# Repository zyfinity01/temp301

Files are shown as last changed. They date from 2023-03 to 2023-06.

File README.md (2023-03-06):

# Open Data Recorder for Environmental Monitoring

An open source and open hardware IoT-connected SDI-12-enabled remote data recorder capable of deployment for environmental monitoring by New Zealand Regional Councils.

## Quick Links

- [Project Charter](docs/charter.md)
- [Meetings](https://gitlab.ecs.vuw.ac.nz/engr489-environment-monitoring/engr489-project/issues?scope=all&utf8=%E2%9C%93&state=all&label_name%5B%5D=Meeting)
- [Development Guide](docs/technical/README.md)

## Project Description

Regional Councils maintain large environmental monitoring networks with real-time data recorded by data recorders being reported via telemetry to virtual servers at a data centre.

This project arose from the desire of the Hydrology Team at Greater Wellington Council to explore the benefits that IoT technologies could offer &mdash; low-cost hardware, low power consumption, future-proof communication technologies and the ability of Council staff to extend the capabilities of the data recorder &mdash; whilst maintaining the sensor accuracy required for scientific studies and regulatory functions. In collaboration with staff and students at the School of Engineering and Computer Science at Victoria University of Wellington, a prototype data recorder has been developed to meet the environmental monitoring requirements of they Hydrology Team.

## Project Requirements

Overarching project requirements are listed in [docs/requirements/requirements.md](docs/requirements/requirements.md).

- Revision 3 requirements are listed in [docs/requirements/requirements_for_Rev 3.0](docs/requirements/requirements_for_Rev 3.0).
- Revision 4 requirements are the same as Revision 3.

## Overall Objectives

- Develop a system to enable more cost effective collection of data to serve the Region's environmental data needs.
- Deliver an 'Open-Source' system that is fully documented which will allow GWRC staff to up-skill and understand IoT concepts and provide GWRC IT department the ability to support the server and data transfer components in the future. Hardware construction would need to be well documented to allow future production of devices post-project.
- Enable future development of the system in collaboration with VUW.
- Develop a system that could be offered to other Regional Councils around New Zealand if successful.

The project can be as big or as small as the project team decides. The main thing is to ensure we end up with a robust, accurate system that can be evaluated against our current systems. GWRC will be able to provide test sites locations and VUW project team will be able exposed to the work the council undertakes - Field trip(s)?

GWRC doesn't have any set funding for the project and monetary contributions can be discussed if the project is of interest to VUW. I should imagine GWRC would be able to pay for the virtual server chargers, software licences and hardware but that is to be confirmed with management.

## Repository Directory Structure

### High level overview

```text
Environmental-Monitoring-2020/engr489-project/
├── docs
├── software
    ├── device
        ├── embedded
        └── webapp
    ├── server
    └── simulator
├── hardware
├── util
└── venv
```

### `software`: Embedded Software and Device Simulators

#### `device`: Embedded Software, Web-App Code

```text
device
├── build
├── embedded
└── webapp
```

- `build`: automatically created by the software build script, `build.sh`.
- `embedded`: Micropython device code &mdash; development takes place here.
- `webapp`: preact web app code &mdash; development takes place here.

#### `server`: scripts for communication with remote servers

```text
server/
[no subdirectories]
```

Python scripts for publishing to an MQTT broker and subscribing to topics. Also contains a Python script for publishing to Microsoft Power BI <https://powerbi.microsoft.com/>. Used during exploration of different protocols for transmitting data from the data recorder.

#### `simulator`: Simulation Scripts

```text
simulator/
[no subdirectories]
```

Various scripts for simulating different parts of the project.

### `docs`: Documents and Documentation

```text
docs
├── bom
├── datasheets
├── development
├── literature
├── meetings
├── presentations
├── reports
├── requirements
├── research
└── technical
```

- `bom`: Bill of Materials (BoM) documents sent for PCB manufacture.
- `technical`: technical documentation, including documentation of the tinyweb server implementation which runs on the ESP32 to provide a web interface to the data recorder.
- `literature`: A flat folder containing PDF copies of anything that will or could be cited in the reports: journal articles, tech notes, etc.  There should be a BibTeX .bib bibliography file at the same level as the PDF files, for use with the JabRef open source bibliography and reference manager.
- `meetings`: saved emails from the 2021 Honours project.
- `presentations`: The files used in any presentations, including the ENGR 489 course final presentation.
- `reports`: Contains the ENGR 489 course reports. There are two reports required this year, a Preliminary Report and a Final Report. LaTeX source files. R, Matlab, etc. files, containing only the figures used in the report at this level. One sub-folder "Figures" to keep figures organised.
- `requirements`: documentation provided by the clients for project requirements.
- `research`: Embedded software, Web App, Hardware Design and PCB development notes.

### `hardware`: Data Recorder Hardware

```text
hardware/
├── reviews
└── schematics
```

- `reviews`: documentation of schematics and PCB reviews.
- `schematics`: electronic schematics and PCB designs of the current revision.

### `util`: utility scripts

```text
util/
├── Docker
├── ansible
├── micropython-hitl
├── micropython-software
├── scripts
└── vagrant
```

Build and test scripts, including development and test environment provisioning and configuration scripts, for performing utility functions separate from the software running on the data recorder.

- `Docker`: Dockerfiles to create images used in jobs in the GitLab CI pipeline.
- `ansible`: Ansible playbooks for provisioning development, build and test environments.
- `micropython-hitl`: hardware-in-the-loop (HTL) testing scripts.
- `micropython-software`: Dockerfile for running MicroPython in a Docker container for development and test purposes.
- `scripts`: build and test scripts mostly intended to be run in the CI pipeline.
- `vagrant`: Vagrantfile for testing of provisioning and configuration of HTL build and test servers in a VirtualBox VM.

### `venv`: Python Virtual Environment

Python virtual environment created when the instructions in the _Development Environment_ section of the [Technical Documentation](docs/technical/README.md) are followed.

---

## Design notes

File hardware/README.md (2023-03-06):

# Hardware

Information about the design of the hardware and evaluation can be found in this repository.

We are using KiCad 6.0. For migrate Altium project to KiCad. KiCad 6.0 is not backward-compatible, please update you KiCad to 6.0 to view the schematics and PCB layout.

- [Schematics](schematics/)
- [Reviews](reviews/)
- [Evaluation](power_consumption_Rev3)

---

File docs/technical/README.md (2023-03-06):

# Technical documentation

This directory stores the technical documentation for the project.

Subdirectories and pages:

- **architecture** - Architectural Documents.
  - **configuration** - device software configuration outline
  - **embedded_sw_architecture_** - outline of the embedded device software architecture
  - **webapp_architecture** - outline of the webapp architecture (frontend)
  - **webserver** - REST API reference for the on-device web-server
- **dev_environment_setup** - instructions for getting started with this repository
- **hardware_setup** - instructions for setting up the device hardware
- **micropython_build** - instructions for building micropython from source and uploading custom firmware to the device

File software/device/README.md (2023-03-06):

# Device Software

This directory holds the following subdirectories and files:

```text
device
├── build/
├── embedded/
├── webapp/
└── build.sh
```

- `build`: automatically created by the software build script, `build.sh` (see below).
- `embedded`: Micropython device code &mdash; development takes place here.
- `webapp`: preact web app code &mdash; development takes place here.
- `build.sh`: a build script that combines the output of the build scripts in the subdirectories, `build-webapp.sh` and `build-device.sh`, into a ready-to-upload `build/` directory with compiled micropython and preact code.

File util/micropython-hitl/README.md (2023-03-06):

# HITL Testing

## Resources

- [good introduction to using rshell](https://blog.miguelgrinberg.com/post/micropython-and-the-internet-of-things-part-iii-building-a-micropython-application)

## Process

HITL (Hardware in the loop testing) is a method of testing that integrates real hardware in the test process.
The `hitl-tests.sh` script first uploads the latest code to the device using `rshell`, then uses `pyboard.py` to copy the device test suite into ram and then run it.
The script greps the test output for "FAIL" and returns an error code if failures were found.

## Runner Setup

The HITL runner is currently on a raspbery pi model 3 B+ with a fresh install of Rasbian Buster.

Setup instructions:

Connect the HITL device via USB. Install apt package `picocom` and test serial communication works with `pycocom /dev/ttyUSB0`

Install gitlab-runner

```shell
curl -L https://packages.gitlab.com/install/repositories/runner/gitlab-runner/script.deb.sh | sudo bash
sudo apt-get install -y gitlab-runner
```

Register the runner

```shell
sudo gitlab-runner register
```

Add gitlab-runner user to dialout and tty groups

```shell
sudo usermod -aG dialout gitlab-runner
sudo usermod -aG tty gitlab-runner
```

Manually install packages onto the runner

```shell
sudo pip3 install pyboard rshell
```

---

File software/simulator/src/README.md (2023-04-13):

# Simulators

This directory contains two scripts:

- `device.py` - A device simulator, used for generating random data for testing the cloud components of this project
- `webserver.py` - A [flask](https://flask.palletsprojects.com/en/2.1.x/)-based script intended to be an API-compatible simulator for the device web-backend. It's used to test the web-app frontend.

Note: Ensure you have your virtual environment initialised and dependendencies from the top-level `requirements.txt` installed.

## Device Simulator

<!-- Refer to #548 -->

### Device Simulator Setup and Execution

1. Copy `device.example.conf` to `device.conf` and edit the defaults (if required)
1. run `python simulator.py [--help]`

### Configuration

| config option | default | description                                                                          |
|---------------|---------|--------------------------------------------------------------------------------------|
| port          | 1883    | broker port                                                                          |
| wait-time     | 3       | number of seconds to wait between attempting to send each message                    |
| device-type   | sdi-12  | type of device (can either be `sdi-12` or `rainfall`                                 |
| verbose       | False   | verbose logging                                                                      |
| format        | json    | Message format (json or csv)                                                         |

## Webserver Simulator

No setup is required to run the `webserver.py` script. Note, however, that paths to the webapp and configuration files are hard-coded into the script.

The simulator can be run from the command line, while at the repository top-level, by executing the command `python software/simulator/src/webserver.py` which will produce the following output (example):

```shell
$ python software/simulator/src/webserver.py
 * Loading JSON from software/device/embedded/src/services/config.example.json
 * Loading JSON from software/device/embedded/src/services/data.example.json
 * Serving Flask app 'webserver' (lazy loading)
 * Environment: production
   WARNING: This is a development server. Do not use it in a production deployment.
   Use a production WSGI server instead.
 * Debug mode: on
 * Running on http://127.0.0.1:5000 (Press CTRL+C to quit)
 * Restarting with stat
 * Loading JSON from software/device/embedded/src/services/config.example.json
 * Loading JSON from software/device/embedded/src/services/data.example.json
 * Debugger is active!
 * Debugger PIN: xxx-yyy-zzz
```

As indicated in the Flask output, the webapp can be viewed by visiting <http://127.0.0.1:5000> in a web browser. Web server activity will be logged to the terminal (example):

```shell
127.0.0.1 - - [10/Oct/2022 15:07:14] "GET / HTTP/1.1" 200 -
127.0.0.1 - - [10/Oct/2022 15:07:15] "GET /bundle.b5e19.css HTTP/1.1" 200 -
127.0.0.1 - - [10/Oct/2022 15:07:15] "GET /bundle.2dea9.esm.js HTTP/1.1" 200 -
127.0.0.1 - - [10/Oct/2022 15:07:15] "GET /data HTTP/1.1" 200 -
127.0.0.1 - - [10/Oct/2022 15:07:15] "GET /config HTTP/1.1" 200 -
127.0.0.1 - - [10/Oct/2022 15:07:15] "GET /favicon.ico HTTP/1.1" 200 -
127.0.0.1 - - [10/Oct/2022 15:07:15] "GET /assets/icons/apple-touch-icon.png HTTP/1.1" 200 -
```

The `webserver.py` simulator may be exited by pressing `Ctrl-C`.

---

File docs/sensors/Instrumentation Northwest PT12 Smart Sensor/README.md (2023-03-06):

# Instrumentation Northwest

The Instrumentation Northwest Inc. sondes made available to us for development and evaluation are PT12 pressure and temperature Smart Sensors.

Instrumentation Northwest, Inc. <https://web.archive.org/web/20180330105810/http://inwusa.com/> became Seametrics <https://www.seametrics.com/> by 1 May 2018. Only a couple of PDFs are downloadable from the Internet Archive page for the PT12 sensor [2].

Seametrics' page has specifications and instructions for the latest version of the PT12 [3] which have been downloaded to this directory.

1. Products - Smart Sensors <https://web.archive.org/web/20160221212342/http://inwusa.com/products/smart-sensors/>
1. Smart Sensors - Pressure & Level - PT12 <https://web.archive.org/web/20160308074848/http://inwusa.com/products/smart-sensors/pressure-and-level/pt12/>
1. PT12 Pressure & Temperature with Modbus & SDI-12 Interface <https://www.seametrics.com/product/pt12/>

---

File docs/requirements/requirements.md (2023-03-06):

# Requirements

## Device Requirements

- Low powered
- Accurate timekeeping
  - Synced with time server
  - Timestamped to NZST (UTC+12)
  - Timestamp to nearest second
- Connected to 12V battery (lead acid, gel, AGM SLA)
  - Battery connected by screw/push terminal
  - Device should retain settings when powered down
  - Possibility of connecting solar panel or 12V AC adapter, so device should be capable of handling any voltage fluctuations
  - Overvoltage and reverse polarity protection
  - Lifetime of 3-6 months
- Wireless comms to mobile device for configuring
  - Bluetooth or WiFi
  - Activated by switch
- USB port for programming device (and maybe diagnostics)
- Wireless data transmission via Vodafone NB-IoT
  - Band 28
  - External antenna connection (SMA)
  - Data transfer protocol to ensure no data loss
- Appropriate size for fitting in raingauge or a galvanised pipe
- Consider ability to add Glyn pulse coherent radar
- Nice to have offline mode where device is out of range of NB-IoT
  - Removable modems to reduce cost of offline devices
  - Physical or in-app switch to toggle modem on/off.
  - Needs to have accurate timekeeping
- Data saved to device on SD card
  - Readings for each unique parameter will have an ID
  - Should contain ID, timestamp, reading
  - Needs accurate timekeeping
  - Need to be able to measure used/free space
- Cost between $200-$300 per device

### SDI-12

- Use SDI-12 communications protocol
- Relay to power up SDI-12 sensor
- User can schedule sensor readings manually
  - Device needs to automatically schedule readings to account for the time to start the sensor and take the reading

### Raingauge

- Ability to monitor 1 (preferably 2) inputs from reed switch triggering
  - With switch debounce
- Up to 1 reading per second
  - Timestamp to nearest second
- Send data every 5 minutes during rain, reduce to hourly (or 6-hourly) transmission when not raining

## Cloud Requirements

- Hosted on a virtual server
- Flexible data storage format to allow future integration with GWRC databases
- Explore possibility of enabling data transfer to FTP server using existing supplier's XML format
- View data in tabular and graph format
  - Identify missing data
  - Identify comms failure
- Send email/SMS for specific data
  - send for missing data, comms failure, system issues
- Daily transmission of SD card capacity

## App Requirements

### Configuration (App -> Device)

- Sensor Settings
  - Recording interval
  - Calibration multiplier (span)
  - Calibration offset (zero)
- Data transmission interval
- Physical location (use phone GPS) - optional
- Device ID and Name
- ability to put the device into "test mode" - temporarily disabling sending data to the cloud backend while calibrating the sensors
- send test message to cloud button
- Synchronise clock to cellphone clock. Useful for sites out of range of NB-IoT
- Set the SDI-12 sensor address on the app and specify ID of the variable being recorded - have a text name and the ability to specify units for measurement variables
- Some SDI-12 sensors take some time to boot up, so allow this time to be configured
- Assign units - mm/h for example

### Visualisation (Device -> App)

- No need to display graphs on the app, but do want live values
- Downloading device data from a specified interval
- number of sent/failed transmissions
- "Download all data" button
- most recent transmission
- most recent reading (for calibration)
- Device battery level
- Network reception level - Signal strength test (in -dBm) - only update this reading on request, no need to constantly poll
- Rainfall totals - because they visit every 2-3 months, they want to calibrate the total recorded rainfall against a level in a collection tank for QA purposes
- Used/free space on SD card

---

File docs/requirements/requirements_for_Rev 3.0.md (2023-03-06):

# Requirements

This document is about the requirements for the Rev 3.0 prototype.

- Improve power efficiency

  - All in one PCB (merge base board and extension board)
  - Use a different 12V to 5V regulator (TPS562201DDCR)
  - Upper limit of the current draw of the whole system is 8.2 mA

- Improve ease of use

  - Use fuel gauge IC to monitor battery state of charge (bq34z110)
  - Change though holes components (Inductors,RGB LEDs, hall effect sensors etc) to surface mount as well as ESP32 microcontroller
  - Use USB to UART interface for programming and debugging the ESP32

- Old problems to fix

  - Fix the reverse polarity protection (currently not working properly)
  - Fix the PCB layout of the power terminals (currently positive and negative labels are inverted)

- Environment Data

  - Water level, flow sensor
    - SDI-12 interface
    - Powered by 12V
  - Accurate timekeeping
    - Time from cellphone tower
    - Time from Real Time Clock (RTC)
  - Data saved to device on SD card
  - Rain gauge data
    - Record the pulse signal from rain gauge
    - Use external counter (flip-flops) circuit to store the data
    - Use a multiplexer to read the binary data when device wakeup
    - must be operating while microcontroller is in deep sleep

- Offline mode where device is out of range of any cellular network

  - Removable modems to reduce cost of offline devices
  - Physical or in-app switch to toggle modem on/off
  - Use onboard Real Time Clock (RTC) to have accurate timekeeping
  - Data storage on SD card

- Communication

  - Use u-box SARA-R4 NB-IoT modem
    - UART interface
    - Wireless data transmission via Vodafone NB-IoT
    - Wireless data transmission via Cat-M1 (Maybe)

- PCB Size

  - Appropriate size for fitting in rain gauge or a galvanised pipe
  - Approximately 13 cm x 17 cm

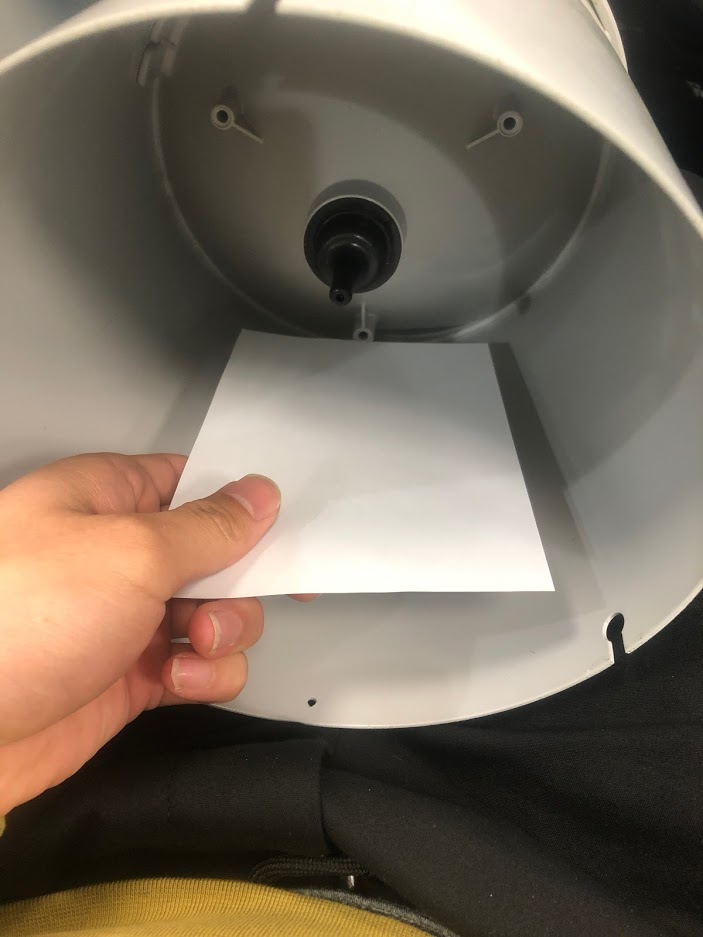
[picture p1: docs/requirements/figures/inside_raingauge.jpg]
Raingauge inside view


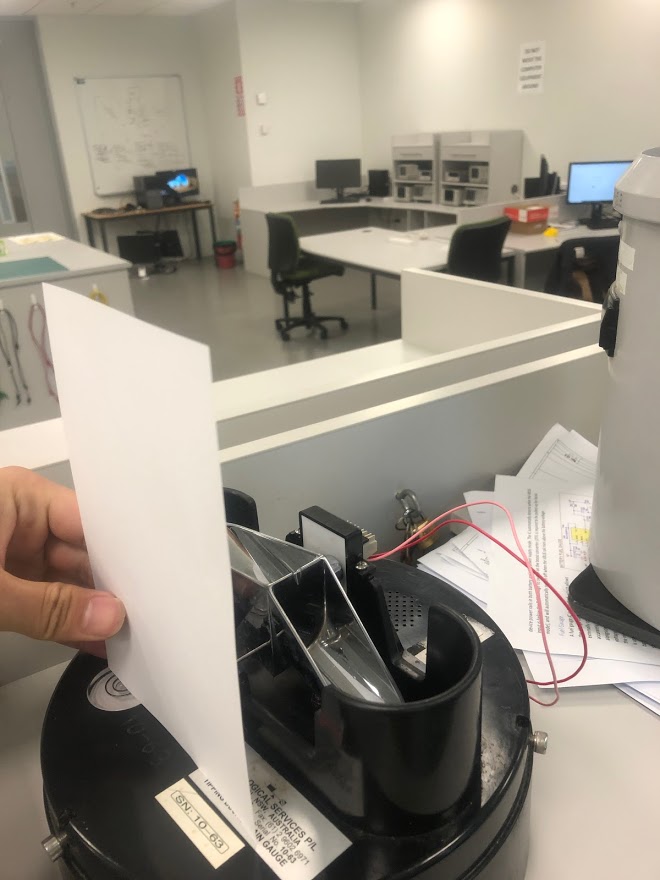
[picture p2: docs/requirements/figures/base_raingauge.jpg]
Raingauge base view


- Cost
  - Cost between $200-$300 per device

---

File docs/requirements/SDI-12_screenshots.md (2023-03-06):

# SDI-12 Configuration in HyQuest Data loggers

Screenshots to detail the process we would follow to achieve the outcomes we want with our current equipment.

We would power-up the SDI-12 sensor using the Digital Output (Relay supplying 12v) on a schedule. In the example below we’re assuming the sensor takes 20 secs to power up ready to take a measurement and we want the measurement taken on the prime 15 minute (0,15,30,45 mins).

HyQuest equipment only allow schedules to start and finish to a resolution of a minute so we would power up the sensor at 14 minutes ready for the 15 minute logged value.  We’d prefer to set schedules to the second resolution if possible?

The Sensor will be powered up for 120 secs and the process will be repeated every 15 minutes.



We set up the SDI-12 Device.

In this example it is a Shaft Encoder with address ‘zero’ and we’ve chosen to use the ‘M’ command for measurement.  Other options are ‘MC’ for measurement with checksum, ‘C’ for concurrent and ‘CC’ for concurrent with checksum (I think)

We’ve set the sensor up to send the measurement command to the SDI-12 device at 14mins 50 secs past the hour and then at an interval of 15 minutes onwards.  That gives the logger 10 secs to retrieve the measurement from the sensor before the data is ‘logged’ at the prime 15 minute interval.

There’s something going on behind-the-scenes at this point.  If we we’re sending the commands manually via a terminal program we’d have typed 0M!, to which the SDI-12 device will have replied with a string along the lines of 002.  The first zero is the SDI-12 device’s address followed by the number of seconds it will take the sensor to have a value ready for retrieval, in this case 2 seconds.

After waiting 2 seconds a zero would appear on the Terminal screen indicating the measurement has been taken. We’d then issue the ‘give me your data command’ 0D0! Would return the last reading from sensor address zero.  The device would then return the data string.

We don’t see any of that going on in the set-up page, so all that timing and back-and-forth must be programmed into the device.

**Note: The data strings retrieved from the device are saved to a temporary storage location in the logger.**



Next we set up the individual ‘sensors’ – basically the recorded variables / parameters from the different SDI-12 sensors attached to the device.

This example is Water level which is derived from SDI-12 sensor address ‘0’ which is aliased as ‘HS Shaft Encoder’ in the previous set-up screen. That isn’t really necessary for our device we could easily just use the address number.

Then we tell the device which variable we want to record from the returned data string from the sensor.  In this case water level is the first variable in the string.

We tell the logger that we want to apply a multiplier of 1000 (converting meters to millimetres) and an offset of zero to the returned value. **Note: Multiplier is always applied before offset in our calculations.**



Then we tell the logger how often we want the values to be recorded to the data logger’s permanent storage.  In this case every 15 minutes.

On the prime 15 minute mark, the data logger accesses the store string in the temporary storage location, extracts variable 1 applies the multiplier and offset calculations and stores the time-stamped value in it’s permanent memory.

**Note 1:** We **REALLY** like recording data on the prime minute (no seconds) with SDI-12 sensors. I guess it’s just ‘tidy’ so that values from different sensors / sites can be compared easily in data management suites, and for environmental monitoring a few seconds either way from the exact time isn’t all that important. It’s up to us to get the timing of sensor data retrieval as close to that prime point as possible.

That said if rounding to the minute is an issue on the device we could just accept that we’re having second values recorded and ‘knock’ them off in the data management on the server?

**Note 2:** We **REALLY** like recording rainfall data to the nearest second as the pulse is recorded on the device. This helps with sub-minute rainfall intensity analysis.



---

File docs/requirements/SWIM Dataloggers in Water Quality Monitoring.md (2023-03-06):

# Regional council use of continuous data loggers in water quality monitoring

The use of continuous loggers for water quality monitoring and investigations was discussed at the last SWIM meeting (3rd & 4th of May 2017). I also collated information of the LAWA website and contacted Environment Southland, the Otago Regional Council and the Greater Wellington Regional Council for information on their programmes.

In summary (Tables 1 and 2):

Many councils use sediment autosamplers, continuous DO sondes and turbidity loggers on a ‘roaming’ / investigation basis. Some councils (GW, ES, ORC, Horizons) started to use optical sensors for nitrate. ORC and ES reported good results for optical sensors, but not for ion selective electrodes (IS). Challenges are power supply and flow adjustment of continuous data. All lake buoys in shallow coastal lakes seem to include a phycocyanin (PC) sensor as proxy for cyanobacteria. Some trials are underway for continuous monitoring of E.coli (ColiMinder). Continuous monitoring has rarely been required as consent monitoring. A detailed list of equipment used by regional councils can be found in Table 3.

Additional notes from the SWIM meeting:

- NIWA is conducting a review of the ORC’s long term water quality monitoring.
- Dean Olson from the ORC pointed out issues comparing spot measurements vs. continuous data, as even the time of day the samples were collected can matter.
- Exo-NO3 was not recommended by GWRC, but others are happy with the YSI-Exo products in general.
- NIWA is trialling ColiMinder in Porirua for 3 years, Andrew Hughes and led by Megan Oliver at GWRC.
- NIWA is looking at relationship between turbidity and clarity in rivers to E. coli concentrations (Rob D-C).

**Table 1:** Regional Council use of continuous monitoring tools in lakes and coastal environments.

| Council | Lakes | Full WQ | Lake level | DO, temp | Turbidity | Comments |
| --- | --- | :---: | :---: | :---: | :---: | --- |
| **Northland** | Whangarei harbour, “buoys in estuaries” |  |  |  | &#x26AB; |  |  |
| **Auckland** | Pupuke (installed), Ototoa (scheduled) | &#x26AB; |  |  |  |  |  |
| **Waikato** | 4 lakes & 1 estuarine buoy | &#x26AB; |  |  |  |  |
| **Bay of Plenty 1** | Rerewhakaaitu, Okareka, Okataina, Rotoma, Rotomahana |  | &#x26AB; |  |  |  |
| **Bay of Plenty 1** | Okaro, Rerewhakaaitu, Rerewhakaaitu, Rotoiti, Rotorua, Tarawera | &#x26AB; |  |  |  | Operated by Waikato University or in partnership |
| **Hawkes Bay** | Lakes Waikaremoana, Tūtira |  |  | &#x26AB; |  | Also have coastal Exo sonde |
| **Horizons** | Horowhenua |  |  |  |  |  |
| **Wellington** | Wairapa (scheduled) | &#x26AB; |  |  |  | ColiMinder trial (NIWA) in Porirua harbour |
| **Tasman** | Maito Reservoir |  |  | &#x26AB; |  |  |
| **Environment Canterbury** | Ellesmere, Forsyth, Wainono | &#x26AB; |  |  |  |  |
| **Southland** | Manapouri (planned) shallow coastal lake (planned) | &#x26AB; |  |  |  |  |

**Note:** Water quality buoys (Full WQ) usually measure DO, temperature, chla, phycocyanin (PC) as proxy for cyanobacteria for coastal lakes, and can include lake level, conductivity, salinity and turbidity.

**Table 2:** Regional Council use of continuous monitoring tools in rivers – overview.

| Council | Flow | Temp | DO | Turbidity | Sediment | NO3 | EColi |
| --- | :---: | :---: | :---: | :---: | :---: | :---: | :---: |
| **Northland** |  |  |  | &#x26AB; | &#x26AB; |  |  |
| **Auckland** |  | &#x26AB; | &#x26AB; |  | &#x26AB; |  | <span style="border-radius:100%; background:orange;">&nbsp;&nbsp;&nbsp;&nbsp;</span> |
| **Waikato** | &#x26AB; | &#x26AB; | &#x26AB; | &#x26AB; | &#x26AB; |  |  |
| **Bay of Plenty**  | &#x26AB; | &#x26AB; | &#x26AB; | &#x26AB; | &#x26AB; | <span style="border-radius:100%; background:green;">&nbsp;&nbsp;&nbsp;&nbsp;</span> |  |
| **Hawkes Bay** | &#x26AB; |  | &#x26AB; |  | &#x26AB; |  |  |
| **Gisborne** | &#x26AB; |  |  |  |  |  |  |
| **Taranaki** |  | &#x26AB; | &#x26AB; | &#x26AB; |  |  |  |
| **Wellington** | &#x26AB; | &#x26AB; | &#x26AB; | &#x26AB; |  | <span style="border-radius:100%; background:orange;">&nbsp;&nbsp;&nbsp;&nbsp;</span> |  |
| **Horizons** | &#x26AB; |  | &#x26AB; |  |  | <span style="border-radius:100%; background:orange;">&nbsp;&nbsp;&nbsp;&nbsp;</span> | <span style="border-radius:100%; background:orange;">&nbsp;&nbsp;&nbsp;&nbsp;</span> |
| **Marlborough** |  | &#x26AB; | &#x26AB; | &#x26AB; |  | <span style="border-radius:100%; background:green;">&nbsp;&nbsp;&nbsp;&nbsp;</span> |  |
| **Tasman** | &#x26AB; | &#x26AB; | &#x26AB; |  |  |  |  |
| **Environment Canterbury** | &#x26AB; | &#x26AB; | &#x26AB; | &#x26AB; | &#x26AB; | <span style="border-radius:100%; background:green;">&nbsp;&nbsp;&nbsp;&nbsp;</span> |  |
| **Otago** | &#x26AB; | &#x26AB; | &#x26AB; | &#x26AB; | &#x26AB; | <span style="border-radius:100%; background:orange;">&nbsp;&nbsp;&nbsp;&nbsp;</span> |  |
| **West Coast** | &#x26AB; |  | &#x26AB; | <span style="border-radius:100%; background:green;">&nbsp;&nbsp;&nbsp;&nbsp;</span> |  |  |  |
| **Southland** | &#x26AB; | &#x26AB; | &#x26AB; | &#x26AB; | &#x26AB; | <span style="border-radius:100%; background:orange;">&nbsp;&nbsp;&nbsp;&nbsp;</span> |  |

Orange indicates trial, green planned purchase.

Source data for tables: SWIM meeting, LAWA website, emails from RC scientists.

See Table 3 for detailed information.
 
**Table 3:** Regional Council use of continuous monitoring tools in rivers, detailed information.

| Council | Water quality parameters | Comments |
| --- | --- | --- |
| Northland | Had 3 sites with cont. turbidity & sed. autosamplers (discontinued). 6 turbidity loggers to be deployed. |  |
| Auckland | Sediment auto samplers. Exo sondes. Trialled diffusive substrates for metals. Trialling Coliminder? |  |
| Waikato | Water temperature at 10 sites. Permanent DO, temperature in Waikato River. 18 D-Optos. Short term: 8 sediment autosamplers, 8 turbidity sondes. Will buy acoustic hydrophones for fish/mussels. | Maintenance for DO every week or every month (depending on site). Contracted out maintenance.  |
| Bay of Plenty  | 3 turbidity. 1 DO (permanent). sediment autosampler at 1 SoE site. 4 roaming DO loggers . Looking at one nitrate sensor at key site, one roaming. |  |
| Hawkes Bay | 3 D-Optos at hydro sites. 3 D-Optos roaming. 1 sediment autosampler. |  |
| Gisborne | Not present at SWIM meeting. |  |
| Taranaki | Temperature, DO, turbidity. |  |
| Wellington | Starting: 1 year. 5 sites, 2 weeks to 1 month DO at SoE sites.  | Bought Exo3 for rivers – cond, temp, DO, turbidity (6 in total). |
| Horizons | 5 continuous DO sites since 2011.  Have trialled nitrate at 1-2 sites. Trialling Colilert. |  |
| Marlborough | Exo sonde for investigations. 1 turbidity and DO sonde. A few temp loggers on plains. ooking into purchasing 2 nitrate sensors. |  |
| Tasman | DO, pH, conductivity sondes, HOBOs, all moved around. | Keen to look at continuous sediment monitoring. |
| Environment Canterbury | 4 sediment autosamplers in urban areas.  3 Aqua 600 in hapua. DO, turbidity sondes for short-term investigations. Planning to buy TriOS nitrate loggers for Hurunui & roaming. | Aqua Trolls battery issues. |
| Otago | Two optical nitrate probes (TriOS OPUS) in Kakanui, one for investigations, one to become permanent. Three more to go in Shag River (TriOS NICO). | Tested IS sensors, but data was “rubbish”. Optical sensors have power supply issue. |
| West Coast | pH, DO sondes used on rotational basis. Are considering putting in turbidity loggers at hydro stations. | Flow in Karamea, Buller, Grey, Hokitika and Waiho. |
| Southland | Turbidity, sediment autosamplers. Trialled nitrate optical sensors for 2 years. Looking at expanding to NIWA monitoring sites. | Optical sensors are much more stable that IS, and can include DOC. Challenge is flow adjustment for continuous data. |
| DOC | 2 D-Optos. 6 conductivity. 4 pH meters for research investigations. 1 sonde. |  |

_Source data for tables: SWIM meeting, LAWA website, emails from RC scientists._

---

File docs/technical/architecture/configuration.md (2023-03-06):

# Device Configuration Schema

This document standardises the device configuration JSON file and API schema, discussed in #161 and in other places.
It should be the source of truth and used as reference.

## Device Configuration

- device_name: str
- device_id: str
- hardware_revision: str
- send_interval: int (mins) - multiple of record_interval
- first_send_at: int (unix time)
- wifi_ssid: str
- wifi_password: str (hashed)
- maintenance_mode: bool
- mqtt_settings: dict
  - host: str
  - port: int
  - username: str
  - password: str
  - parent_topic: str
- mmw_settings: dict
  - auth_token: str
  - sampling_feature: str
- sdi12_sensors: list
  - sensor_name: str
  - enabled: bool
  - address: char/byte/string
  - bootup_time: int (seconds)
  - record_interval: int (mins)
  - first_record_at: int (unix time)
  - readings: list
    - reading: string
    - index: int
    - unit: string
    - multiplier: int (mm)
    - offset: int (mm)
- rainfall_sensor: dict
  - enabled: boolean
  - record_interval: int (mins)
- adc_calibration: dict

## Device Data

dynamic data file (json): stores dynamic data generated by the controller.

- last_updated: int (unix time)
- last_transmitted: int (unix time)
- battery_level: int (voltage)
- coverage_level: int (dBm)
- messages_sent: int
- failed_transmissions: int

## Notes

- [Signal Strength measures](https://wiki.teltonika-networks.com/view/RSRP_and_RSRQ)

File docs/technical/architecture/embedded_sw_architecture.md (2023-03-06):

# Embedded Software Architecture

Constructing an efficient software architecture for the devices is
important for reliability, testing and ease of collaboration.
This section focusses on the high-level software design, including the modes of operation and web server design.
Readers are encouraged to refer to the [2020 hardware report](/docs/literature/Behrent2020FinalReport.pdf) for low-level device software design.

- [Embedded Software Architecture](#embedded-software-architecture)
  - [Constraints](#constraints)
  - [Modes of Operation](#modes-of-operation)
  - [Architecture Overview](#architecture-overview)
  - [Web Server Design](#web-server-design)
    - [Server-side vs Client Side Rendering](#server-side-vs-client-side-rendering)
    - [REST API](#rest-api)
  - [Configure Mode - Web Server Implementation](#configure-mode---web-server-implementation)

## Constraints

The design of the device software is constrained to suit the low-power hardware chosen for the project.
Specifically, the ESP32 microcontroller has 8MB of RAM, and 4MB of non-volatile "disk" (flash memory) space.
The RAM constraints may potentially be reduced to 100KB in the future to free up some hardware pins and reduce power usage.
Moreover, to obtain maximum power savings,
the device needs to be in "deep sleep" - extremely low power mode where nearly everything is turned off - for as long as possible.
The software needs to be designed around this.
In deep sleep mode, no code can run, so all the processing required should be done in batches before resuming deep sleep.

## Modes of Operation

The high-level software is split into two main logical "modes": `regular mode` and `configure mode`.

- `configure mode` is initiated by the user via pressing a push-button or activating a hall-effect sensor with a magnet.
  It starts a WiFi access point and the webserver which allows the user to modify configuration values of the device.
  Once the user has finished configuring the device, a pushbutton or time-out would return the device back to sleep, or into regular mode if the user was configuring the device when a scheduled reading was meant to take place.
- `regular mode` is the regular operation of the device.
  When the device boots up from deep sleep, it takes a reading of the SDI-12 sensor, and periodically transmits the data to IoT Central before going back to sleep.

This separation was chosen because it logically matches the two main use cases of the device - *Configuring the device* and *Monitoring the state of a river*, allowing for a workflow shown in the following figure:

```mermaid
flowchart TD;
  Start[Device Boots/Wakes from Sleep] --> Boot{{Boot Reason}}
  Boot-- pushbutton wake -->Conf[go into configure mode]
  Conf --> U[User configures Device] --> Sched{{Scheduled Reading Missed?}}
  Sched -- no, return to sleep -->Start
  Boot-- Deep Sleep Timeout --> Collect
  Sched-- yes, enter regular mode --> Collect
  Collect[Collect SDI12 Sensor Reading] --> Near
  Near[Near send_interval?]-- yes --> Transmit[Transmit Data to cloud]
  Near-- no --> Start
  Transmit-- return to deep sleep -->Start
```

## Architecture Overview

The figure below shows a stack-diagram overview of our multi-tiered device-code architecture, building upon the existing community-provided micropython firmware.
At the top level, the high level code is responsible for handling the "pipeline" of regular operation as well as enabling/disabling the webserver.
The high level code makes use of different "services" - logically grouped functions and classes for particular device functionality, such as the webserver or device configuration.
In turn, the services directly use community-provided libraries.
They also need to communicate with the hardware.
Low-level device drivers act as a translator between hardware devices and the high-level software, abstracting away the technical details and providing a common interface so that high-level code can be written independently of the specific hardware.
At the bottom layers, firmware compiles high-level python code into low-level bytecode which is run by the micropython virtual machine on the ESP32 hardware.
External hardware, such as the modem and SD Card reader, are communicated with via serial communication busses on the ESP32.

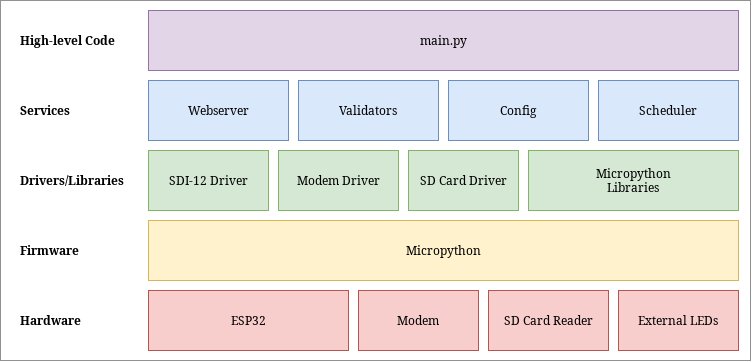
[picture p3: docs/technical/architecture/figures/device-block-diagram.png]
device block diagram


Designing the software in this way allows for multiple benefits:

- *Separation of concerns*: components in each layer should only
    communicate with adjacent layers.
    In theory, this decouples the
    components so that layers can be modified without affecting the rest
    of the stack.

- *Increased Collaboration*: By agreeing on shared interfaces between
    layers, one team member is able to work on the high-level software
    while the other can work on low-level code without fear of
    interfering with each-other.

- *Increased Testability*: Each layer can be tested in isolation,
    making it easier to perform unit and integration testing.

Other possible architectures were also considered: The best alternative, known as "feature oriented architecture", takes cues from Service-Oriented Architecture (SOA), a pattern commonly seen in the web-development industry.

In this style, each high-level logical component of the system is encapsulated into it's own "service" with it's own dependencies, effectively splitting the architecture shown above into columns rather than rows.
This style promotes loose coupling between the different modes of operation on the device, which allows for independent development of different features, as well as easier testing.
However, a feature-oriented style doesn't work particularly well in this context due to the high amount of shared resources.
Hardware device drivers, for example, must be a singleton: only one instance of the driver can exist.
This approach would work in a more modular hardware design - like with independent microcontrollers for separate functionality on the device - but for a proof-of-concept, this would only add needless complexity.

## Web Server Design

The Web Server - the *backend* - is responsible for serving up the Web App to the client - the *frontend*.
The web server is designed around a webserver library called [TinyWeb](https://github.com/belyalov/tinyweb), a lightweight, single-threaded HTTP server for Micropython.

Various other webserver libraries were researched and tested, including [MicroWebSrv](https://github.com/jczic/MicroWebSrv), [MicroWebSrv2](https://github.com/jczic/MicroWebSrv2) and [Picoweb](https://github.com/pfalcon/picoweb), but each had [major issues](/docs/research/software/mobile-app/microwebsrv-test/README.md) which limited their functionality.

### Server-side vs Client Side Rendering

Choosing whether to use server-side rendering or client-side rendering for the Web App was an important design decision.
Server side rendering (SSR) is when the server is responsible for creating the entire web page, and then sending that to the client.
If the page requires dynamic data (for example, results from a sensor reading), the server populates the page with dynamic data using a *template engine.* This method works well for normal webservers, because they usually have high compute capacity and are able to dynamically render multiple webpages at once.
 However, the low CPU and RAM constraints on the microcontroller hardware mean that building websites on the device would be both slow and power consuming.

Client-side rendering (CSR) is a newer approach made possible by modern frameworks such as [React](https://reactjs.org/), where the compilation of dynamic content and generation of the webpage is undertaken by the client web browser.
The webserver sends the static HTML and CSS to the browser, and the browser uses the webserver's API via asynchronous javascript calls to get the dynamic data.

This approach is preferred in this situation because it keeps the webserver resource demands on the device as light as possible.
The other major benefit is caching.
Caching with SSR is difficult on a microcontroller due to the resource constraints, and so the server needs to send the entire page every time.
A client, meanwhile, can cache repeated requests, which means subsequent configuration attempts only require getting the dynamic data.
This improves page loading times significantly and reduces the load on the webserver.

### REST API

The REST API endpoints are documented [here](webserver.md)

## Configure Mode - Web Server Implementation

One of the requirements for configure mode is to have it cancel with a physical button press, or a timeout in case the user forgets.
 Cancellation via button is performed by a hardware interrupt that cancels the asyncio webserver task and closes the event loop.
To cancel via timeout, a modification to the webserver is required.
This is implemented by a subclass of the Tinyweb server which contains a Watchdog timer, and overrides the server's `_handler()` method - responsible for handling incoming requests.
When a request is handled, the overridden method resets ("pats") the watchdog, and then passes control to the original parent method for actual handling.
If the watchdog times out, a callback method for shutting down the server is called.
Implementing the webserver this way meant that the original library code is preserved, and the modifications are visible at the "service" level.

The webserver implementation is built on the idea of *Resources* - arbitrary Python classes with methods defined for different HTTP request types, representing a logically defined object with it's own state and operations.
This is a fundamental aspect of RESTful design.
Whilst tinyweb supports python generators, Micropython doesn't distinguish between generators and asyncio coroutines.
We implemented a modification to the library to support coroutines in resources.

At the top level, resources are mapped to a URL.
However, the implementation of the mapping differed from the design - TinyWeb doesn't support nested endpoints, so the dynamic part of a URI must always be at the end.
For example, the resource URI `/config/sdi12/<sensor_name>/test` (where `<sensor_name>` is dynamic) would be invalid.
To get around this, the API was modified to place the action - "update, rename, test" etc - before the dynamic part.

Each resource that accepts user data needs to perform validation to ensure the configuration values are set correctly.
To do this, a generic [validation service](/software/device/embedded/src/services/validators.py) was written that could validate any arbitrary data, modelled on the validation functions of the Django webserver framework.
The service is capable of recursively validating nested JSON inputs, and is used extensively across the codebase to ensure data consistency.

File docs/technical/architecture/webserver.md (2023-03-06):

# Web Server Documentation/REST API

This page documents the web server used in the configuration mode of the application.

## REST API Endpoints

### Device Data

Endpoint for data visualisation.

#### GET `/data`

Returns the device data JSON file. [Response Content](configuration.md#device-data)

### Device Config

#### GET `/config`

Returns the device configuration JSON. [Response Content](configuration.md#device-configuration)

#### POST `/config`

Update device common configuration.
This endpoint accepts any data aside from the sdi-12 sensor specific data defined in the [Configuration schema](configuration.md) (see [below](#sdi-12-sensor-config))

### SDI-12 Sensor Config

Tinyweb doesn't seem to support nested endpoints after a parameter, so things like `/test/<name>/nested` won't work.
As a result, the API isn't completely "restful".

#### POST `/config/sdi12/update/<name>`

Update a specific SDI-12 sensor. `<name>` should not contain spaces.
If `<name>` does not exist, it will create a new SDI-12 sensor.

#### POST `/config/sdi12/rename/<name>`

Rename the SDI-12 sensor. Request body must be json-encoded and contain `"name":"new_name"`

#### POST `/config/sdi12/delete/<name>`

Delete the SDI-12 sensor.

#### GET `/config/sdi12/test/<name>`

Test a specific SDI-12 sensor.
The device must be in `configure` mode (ie, the configuration file must have `configure-mode` enabled).
returns:

```json
{
    "response": "" // the response from the test
    "error"?: "" // optional error response
}
```

### SDI-12 Monitor

Allows raw SDI-12 commands to be sent to the device, and the untransformed output to be interpreted by the user.

#### GET `/monitor?command=!?`

Where the value of `command` is the SDI-12 command to send to the device (such as `?!`)

returns the following response as json:

```json
{
    "response": "", // response string from the command output
    "command": "",  // the command that was sent to the device
    "error"?: ""    // optional: an error string
}
```

query parameters don't seem to be supported by the REST API "resource" class in the tinyweb implementation.

### Time

Allows updating the device time.

#### POST `/time`

force time sync with NTP servers. (not implemented yet)

## Design

Unlike the functionally-programmed "regular-mode", the configure-mode is object oriented, built around the [tinyweb](https://github.com/belyalov/tinyweb/) library.

Each REST API endpoint is represented by a class which implements the HTTP methods as a function.
This class is meant to be stateless, and the functions have a 'callback method' parameter for saving the data.
The function is responsible for checking the incoming data, calling the callback method, and then returning a response to the user.

Some methods can be coroutines, but they must be decorated in a `@staticmethod` so that tinyweb knows what is (see !152).

The webserver itself is wrapped in an outer class called TimedWebServer which implements a watchdog timer, responsible for shutting down the server
if it times out.
This is used to prevent the power-hungry webserver from draining all the device's batteries if the user accidentally leaves the webserver running.
Once it has timed out, the device returns to "regular-mode".

Refer to the Tinyweb documentation for more details.

## Other Notes

sending an empty POST request with the header `Content-Type: 0` will throw a 400 error in the `read_parse_form_data()` method.

---

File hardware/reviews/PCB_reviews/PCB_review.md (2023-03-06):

# Rev 3.0 PCB Review

The footprint for N-MOSFET didn’t match FDN361BN.

Affected component: Q501, Q502

The datasheet of FDN361BN can befound [here](https://www.onsemi.com/pdf/datasheet/fdn361bn-d.pdf).





Gate should be Pin 2 but the footprint is Pin 1.

Solution: update the footprint for the FDN361BN.

GPIO 34 and 35 are input only Pin and we use it for outputting control signal for SDI_EN and SDI_FOut.

Solution: Use GPIO23 and GPIO5

MUX output is high when powered up. This is not an issue when normal operating but we connect this pin to GPIO2 which is a strapping pin for esp32. It must be low or floating to getting into bootloader.

Solution: Remove MUX. Use IO expander to get count and control the counter.



Our client wants the rain data to have in 1min timestamp and the maximum rate the rain gauge can tip is 12tips/minute. So, 6-bits is enough to count.

Do you know what will happen to the battery fuel gauge if we reverse the polarity of the battery? Is there protection in the IC? Or the IC just don’t care?

Currently the I2C terminal uses mail header, could you change to female header?

We have decided not to surface mount the modem on the Rev4.0 but use the LTE shield from Sparkfun instead. It would be nice to have female header for the shield so we can stack the modem on the PCB without the terminal blocks.

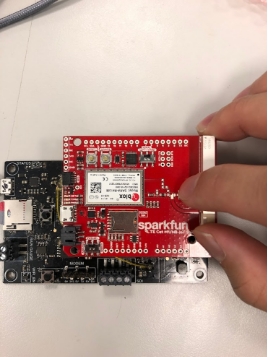
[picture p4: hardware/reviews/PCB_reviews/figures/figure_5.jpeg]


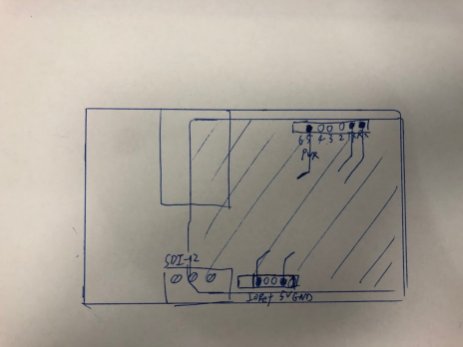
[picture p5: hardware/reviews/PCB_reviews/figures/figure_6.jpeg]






Just avoid any confusion this is the TX/RX for the modem

|ESP32||Modem|
| :-: | :-: | :-: |
|Pin 27 / MOD_RX|\<-|D1 / RX|
|Pin 26 / MOD_TX|->|D0 / TX|

Note that the RX/TX in the modem is reversed.

I think I will still keep the USB to TTL circuit on Rev 4.0.

Remove button for WiFi enable. Use pin header for though hole hall effect sensor.



Only Green and Red LED is used, not connect blue LED. Because run out of GPIO.

Change part for the LED used in reverse polarity protection.

Consider this device is secure in a case some change maybe needed.

For example, the data logger below has:

- SD card socket is inward instead of outward.

- Micro usb socket face toward the user

- A switch to turn on/off the device

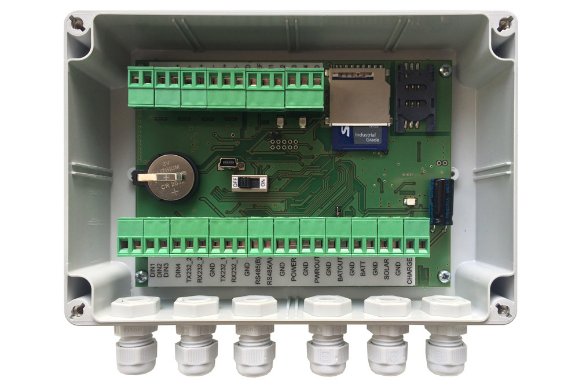
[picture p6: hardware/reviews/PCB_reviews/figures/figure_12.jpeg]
DATA LOGGERS &amp; ACCESSORIES — BARANI DESIGN Technologies


---

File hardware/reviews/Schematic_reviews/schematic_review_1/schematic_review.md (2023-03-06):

# Schematic review 1

This looks good, current roughly: Ireverse = (Vbat – Vdiode – Vled) / 3300 ohm = (14V – 0.2V – 2V) / 3300 = 3.5mA. Power dissipation of the resistor is therefore well below the rating, but the LED is tested at 25mA so it’ll be pretty weak. Not a huge issue.

Do we want to add overvoltage protection here too? For small spikes, take a look at TVS diodes. There are also ICs that do both overcurrent and overvoltage protection.



Response: Not looking to improve the system robustness at this stage, may be in the future generation.

Part number and description don’t match. This is a 1/8W 1% resistor. Didn’t check all parts, but a good idea to go through and check each description just to be sure they match the part number.



Response: I checked all parts (resistors and caps) in yageo serch engine. <https://www.yageo.com/en/Product/Search?target=target_title>

This MOSFET is only rated to 1.5A, it’s pretty small. The system shouldn’t draw that much all the time, but it may do when transmitting from the modem as the peak looks to be 2.4A. It’s best to play is safe and go larger with this one, larger MOSFETs are cheap.



Response: Change to FDN360P which allows Imax = 2A

The switching regulator TPS562201DDCR you’ve chosen has an input voltage rating of 17V. Do we know how high the lead acid battery gets at full charge? I’d suspect it comes very close to that limit, any surge will likely fry the regulator. The peak modem current is also 2.4A, exceeding the rating. Here’s a Digikey search with some filters:

<https://www.digikey.co.nz/short/mbfvnfzh>

Response: The peak current has decreased due to the modem now use only 0.5A at peak, so no exceeding 2A limit. Lead acid battery do not exceeding 17V unless operating under -20°C. This IC is used in many project powered by car battery so I don’t see there is a problem.

Put a 100nF on the input also, 10uF won’t filter out high freq noise, it’s only used for bulk capacitance. Helps with stability.
I’d consider increasing the size of the bootstrap capacitor (package size and voltage rating). On a switch mode this will see some large switching voltages due to the inductor. Better to jump up to a 0805 25V.



Response: Added another 100nF cap (0.1uF). Change bootstrap capacitor to higher voltage rating (0805)

This inductor has no stock in most places: <https://octopart.com/search?q=RLB0912-3R3ML-ND&currency=USD&specs=0> I haven’t checked all your parts but a good idea to do this too. Generate a BoM and take a look, I’d recommend trying to use same brands for parts if you can for passives e.g. yageo/murata for caps and resistors.

I’d also recommend surface mount, in production having TH components is hard to manufacture. The datasheet recommends typical 4.7uH not 3.3uH.



Response: Change to SRN5040-4R7M IND 4.7uH 35mOhm 3.3A surface mount

Is there a reason you went for a LDO for the 3.7V regulator? At the peak modem transmit current we have: P = (5V – 3.7V) * 2.4A = 3.12W. That is a huge amount of power dissipation, the case will get very hot. I’d go switch mode here unless you had a reason for choosing LDO specifically?



Response: New modem uses 3.3V. So, the 3.8V regulator has removed. To replace that, a 5V to 3.3V switch regulator is added.

Assuming this is a place holder, but when you do select an LED remember to use the formula for the resistor: R = (3.3V – Vf) / Iled



This looks like it’s missing a 3V3 net. Also add a bypass/decoupling. Datasheet recommends a 22uF and a 100nF. This looks like it’s a wifi/Bluetooth module, what is the reason for using this module instead of a stand alone microcontroller?



Response: bypass/decoupling caps added.



How are you planning on programming the microcontroller? I’m not sure if I’m missing something, but this is what the datasheet recommends. Says it’s JTAG, looks a little weird compared with the second pic which is a standard 10-pin JTAG.



Response: JTAG interface added.



Response: A USB interface can also be used for programming

LDO input capacitors, I’d suggest a 10uF and a 100nF. The output cap is massive, is there a reason for this?



Response: Linear regulator has been removed.

UART series resistors, probably include some (\< 100ohm). Useful to protect the bus and for prototyping.



Response: Resistor added



I’m not sure I understand from the naming what this circuit is used for, can you explain it for me?



Response: Normally you need to push the boot button when you program the ESP32. This circuit can generate a signal to IO0 automaticly so you don’t need to push the button to upload the program. This circuit is used on most of the ESP32Devkit.

<https://dl.espressif.com/dl/schematics/ESP32-Core-Board-V2_sch.pdf>

I assume this is just unfinished, but the net doesn’t connect to anything I can see and the caps need values.



Response: This modem is no longer used

This SD card holder doesn’t appear to be sold anywhere. I’d choose a more common part.



Response: The actural component can be selected later.

Again I assume this is just not finished, but need to chose an RGB LED and resistor values. Personally I’d chose



Response: I am considering using a surface mount RGB LED module. Like NeoPixel.

Add some decoupling 100nF caps here.



Response: Decoupling caps added.

What values are these resistors. I assume the pull-down is to ensure the mosfet is off when the gate isn’t driven?



Response: This resistor value should be 1M ohm.

This buffer chip absolute max rating is 6.5V on any input. My understand was that SDI-12 is 12V logic-high? Might need to find a higher voltage buffer. I’d also add a 0 ohm resistor in series with the output, in case you need a small resistance to stop the MOSFET switching too fast creating ringing. What is the point of the ForceLO net other than preventing TX from transmitting?





Response: The SDI-12 logic operates from -0.5V to 5.5V. I don’t think it is a problem.

Last point is I’d recommend generating a BoM when you have selected your parts, and have a look for them online to gauge stock availability. Make sure no parts are in last-time buy or obsolete status too.

Response: BOM is in the folder



---

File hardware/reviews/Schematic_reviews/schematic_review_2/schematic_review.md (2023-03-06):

# Schematic review 2

## Rain Gauge Review

All the sensors should have 100nF caps for their 3v3 rails. Just make it a habit to do this for every IC.



Response: Added bypass caps

## Hall Sensor

How does the rain gauge work in operation. I see this is a hall sensor of some kind, are we needing to mount the device in proximity to a magnet? How strong is the magnet, and what orientation? Both are pretty important to the layout.



Looks like you don’t need that resistor on the output of the hall sensor.





Response:

- Hall sensor now change to reed switch to generate a pulse signal.
- The signal is normally on low.
- When a magnet present, the reed switch will open and 5V (High) signal gose to the counter.
- The resistors and cap are on the main board and need a extention wire to place the reed switch near the rain gauge.

## Counter

Worth noting the count will be one ahead because both inputs are connected on the counter as per datasheet below. I didn’t see anything so say we need CPR, could use a 0R between CPC and CPR?







Response: I find a example wireing for the counter online. It shows the CPC and CPR are connected together. Since I have the counter IC, I will test it later.

I didn’t see anything to say that /CE could be left floating, you should ground it to be sure.



Response: CE is STOP bit

It might be worth putting a pull-up on the /MRC line, to be sure we don’t accidently reset the count when the micro is off as the reset is active low.

Response: Pull up resistor added

## Shift Register

I’m not sure I understand why there is a shift register at all. The counter could be connected to a MUX, so all 8 inputs down to 1 GPIO pin. Then the microcontroller can quickly switch through the MUX inputs to get the binary count. Was there another purpose?

Why is /CE connected to 3V3, as it looks like you intend to use the CP input?







Response: Shift register has removed and now using 8bit mux.

## Battery Gauge

Looks like this is just a copy of the circuit diagram from the datasheet, so it’s hard to review without actual component values i.e. the Zener, MOSFETS, resistors, etc. However I would say, unless we want a thermistor on the battery to monitor temperature, the ALERT and circuitry is redundant. Good to have if you are planning on having a thermistor on the battery.



Looks like these are the wrong way around. Datasheet diagram also has them around the other way.





Pick a voltage divider ratio such that: 14V * Rbot/(Rtop+Rbot) = 0.9V







This is a better schematic to use, though note it’s for a 5V battery.



Response:

- My schematic follows the Multi-cell one. With voltage devider resistor = 16.5k ( 17000mV – 900mV)/900mV = 295.2k = 300k

- LED display circuit and Alert is not needed thus not in the schematic

- I think there are more components can be remove since I don’t need 2.5V(REGIN, REG25) but I am not sure. Could you tell me what can be removed?

- The sensor resistor value have not been determined. I am not sure how to calculated the resistence for that.



- There is a footnote for optimize for required voltage and current. I don’t know what that means. Something to do with R2 R3 R4?





---

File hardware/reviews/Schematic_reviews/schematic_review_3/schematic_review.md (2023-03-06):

# Schematic Review 3

## Water Sensor Hub

Put some 100nF caps in here, datasheet doesn’t call for it but they help with filtering the switching noise of the power supply from the output and input.



Response: Cap added

Can you check the stock for this, or chose a part (or a part that has a generic footprint). My experience is that they often don’t have generic footprints for SD card holders, so it needs to be chosen before PCB layout.



Response: Using MEM2075-00-140-01-A from kicad

[Datasheet](https://www.digikey.com/en/products/detail/gct/MEM2075-00-140-01-A/9859614)

[Footprint](https://www.snapeda.com/parts/MEM2075-00-140-01-A/Global%20Connector%20Technology/view-part/?ref=digikey)

## Battery Schematics

Some stuff that can be DNP i.e. we’ll put it on the PCB but don’t place the component when you assemble it.

Do-not-place (DNP) these ones, probably don’t need them:



I can’t find where the SDA/SCL signals are connected to the microcontroller. I2C lines also need pull-ups, use 10K to minimize power draw and lower them if the signals rise-time is too long (makes the square waves look very rounded).



Response:

- SCL: USB_D-
- SDA: USB_D+



Response: Pull up resister added

Not sure if you found something to say ground these, if so ignore, but it isn’t recommended to ground / connect to VCC anything that doesn’t explicitly tell you to do so in the datasheet. I would leave it floating.



Response: Leave unconnected

For the current sense resistor, you need to determine what the total (approximate) current draw of the system will be. The just use Ohms law to chose a resistor
   V=IR => 125mV/Itotal = Rsense

   You don’t plan on drawing more than 1.25A so I’d say you could go for ~ 0.1 ohm/0.25W  resistor. This is assuming the battery won’t be charged while plugged in, and is only connected when powering the system. If that isn’t the case, the current you use will instead be the charging current with some safety factor.



Response: Add 0.1ohm resistor

I noticed these caps (I haven’t checked others but you should) appear to be 0201. That’s pretty small, fine for boards you’re getting PCBA’d and close to finished but horrible for prototypes. I would go 0402 or larger, as 0201 is very hard to solder by hand.



Response: Change all 0201 to 0603 or bigger.

---

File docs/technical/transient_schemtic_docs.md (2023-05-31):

# Transient Protection Docs

## Explanation

Added transient protection circuit from SDI-12 Protocol [docs]( https://www.sdi-12.org/current_specification/SDI-12_version-1_4-Jan-30-2021.pdf).
Included the circuit regarding "sensor or data recorder interface with transient protection", created the spark gap symbol in KiCad and saved it to the repo schematic library. All values of components are taken from the given example schematic.
The arrangement of the transient protection on the PCB will be difficult as the protection needs to be between the CMOS 3-State Buufer and the SDI-12 data line, potentially requiring a rearrangement of the PCB itself.

For any more information, refer to the docs linked above.

---

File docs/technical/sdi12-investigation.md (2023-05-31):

# SDI-12 Investigation

A writeup of all of our research on the sdi-12 system on the data recorder as part of our evaluation

## Script for querying addresses of devices on the SDI12 line

I ran all this code in the repl loop, so writing it up here. Function to run any sdi-12 command on line. Bootleg version of run_command in sdi-12 driver. This function couldn't be used as you need to specify a sensor address, which the address query does not use

```python
def send_cmd(sdi, cmd)
    sdi12._wake_sensors(sdi)
    sdi["dir_"](0)
    uart = sdi["uart"]
    uart.write(cmd)
    time.sleep_us(8333 * len(cmd))
    sdi["dir_"](1)
    r1 = uart.read()
    time.sleep_ms(1000)
    r2 = uart.read()
    return [r1, r2]
```

Once that function has been defined in the repl loop, can run the address query command

```python
from drivers import sdi12
sdi=sdi12.init_sdi()
sdi12.turn_on_sensors(sdi)
r=send_cmd(sdi, "?!")
```

r will contain the returned addresses in the second return value

## Results of script

We found the Rain Gauge has the address 1, and the Water Level has the address 0. We could get the addresses when both were connected or when each was connected individually.

## 12V Line

We also investigated the behavior of the 12V line. One of the requirements to meet SDI-12 protocols is an uninterrupted 12V supply line to each sensor along the SDI-12 bus. The 12V can be sourced from the data recorder or an external 12V supply but it must be a constant supply. The first attempt at investigating the 12V supply led to us using a multimeter and probes, we noticed the voltage across the SDI-12 12V output and ground was the same as the voltage across the power input to the data recorder and ground. We noticed the voltage was initially only reaching 9V, this was due to a faulty power supply to the data recorder. Once the power supply was amended, there was a match between the 12V power supply to the data recorder and the 12V across the SDI-12 12V line and ground. Now we had a consistent 12V being supplied from the data recorder, the next stage was to observe the voltage level of the SDI-12 12V line during normal function and deep sleep mode. We noticed there was a drop in voltage along the 12V line during initialization, after investigating the code we noticed during the __init__ function each sensor is initialized as asleep by default. Having the sensors asleep by default means the SDI enable line was dragged low, this meant the 12V line was dragged low. Directly after the sensors are initialized the turn_on_sensors() function is run and the SDI enable line is put back to high and reads 12V again. While the SID-12 12V line is only pulled low for a very short period, to be SDI-12 protocol compliant this can never happen. To fix this, the code will be edited so sensors are initialized as awake to keep the enable line high, or separate the awake/sleep status of the sensors to a different field and constantly have the enable line high.

---

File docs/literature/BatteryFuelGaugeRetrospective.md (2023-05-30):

# Battery Fuel Gauge Retrospective and Lessons Learnt

## Research we did - summary of datasheets

Background investigation was completed and compiled into a LaTeX document found in issue #15 [LaTex-Document](https://gitlab.ecs.vuw.ac.nz/course-work/engr301/2023/group3/data-recorder/uploads/ea0835b59d4042676c8adcc2486e9ccc/BQ34Z110_Battery_Fuel_Gauge_and_Alarm_Battery_12V_7Ah.pdf). By looking through the datasheet for the BQ34Z110, it was realized that the flash memory on the chip would need to be configured for our particular application to work. I2C communication with the chip would need to be implemented for communication between the onboard ESP-32 microprocessor and the BQ34Z110, there were plenty of examples of how this communication could be achieved with an outline of simple and complicated methods depending on the level of customization. We investigated the supplied 12V 7Ah lead acid battery specified, while this is a standard battery to be implemented with a data recorder, it does limit our options for battery fuel gauge ICs. The selected battery fuel gauge IC needs to be compatible with the internal chemistry of the battery to be able to correctly collect data about the battery, the lead-acid internal chemistry is specified as compliant with the BQ34Z110.

### I2C communication

The ESP32 on the data recorder runs micropython, which has a library for I2C communication. This was used to communicate with the battery fuel gauge to send and receive data between the ESP32 and the BQ34Z10.

The below code initialized I2C and instructs all devices on the line to return their addresses. The BQ34Z110 has an address of 85 for this application, we observed the correct vale returning as well as the manufacturer information using this script.

```python
from machine import I2C
i2c = I2C(0)
i2c.scan()
```

You could then communicate using the below code, where the contents of the array in `bytearray()` were the command to be sent. The list of commands you can use is in the [BQ34Z110-data-sheet](https://www.ti.com/lit/ds/symlink/bq34z110.pdf?ts=1685152355290&ref_url=https%253A%252F%252Fwww.ti.com%252Fproduct%252FBQ34Z110). `0x6e` is the "manufacturer name" command. On reading, the returned bytes would start with "Texas Inst.". In the `readfrom()` function, the second parameter is the number of bytes to be read from the I2C line.

```python
i2c.writeto(85, bytearray([0x6e])
i2c.readfrom(85, 64)
```

## Why it didn't work

We would need to configure the BQ34Z110 for our particular purpose by programming the flash memory. There are default values for all the data flash memory settings, but some would need to be altered to work with the chemistry of the battery as the chemistry affects the rate of discharge and current state of charge. [This](https://www.ti.com/lit/an/slua790/slua790.pdf?ts=1683050503158&ref_url=http%253A%252F%252Fti.com%252Fproduct%252FBQ34110) document reviewed in issue #70 said to use the software provided by Texas Instruments, we tried to chase down the particular software as detailed in issue #71. The first software package that was attempted for use was BQSTUDIO, which was found to not support the BQ34Z110. Software specifically designed for the BQ34Z110 was found on the Texas Instruments website, however, this required hardware - a [BQ34Z110EVM](https://www.digikey.co.nz/en/products/detail/texas-instruments/BQ34Z110EVM/4090776) evaluation module to be used. As the BQ34Z110 is an old chip, this EVM board is no longer manufactured and the correct software required to pair with the board no longer receives updates or functions on any Windows machine older than Windows 7. Due to these circumstances of incompatibility, we conclude that the BQ34Z110 is not fit for purpose for this application, the battery fuel gauge IC needs to be upgraded to a newer version that is still compatible with a lead acid battery chemistry and has up to date software to configure the flash drive.

## How it could be made to work

After looking through data sheets and comparing the information to what we had found in the Texas Instruments forum, this shows that the BQ34Z110 is outdated, and therefore any software that we tried to use was not compatible with it. We recommend using a more up-to-date fuel gauge for this project. An example of one would be the [BQ34Z100-R2](https://www.ti.com/lit/ds/symlink/bq34z100-r2.pdf?ts=1685424793452&ref_url=https%253A%252F%252Fwww.ti.com%252Fproduct%252Fja-jp%252FBQ34Z100-R2%253Futm_source%253Dgoogle%2526utm_medium%253Dcpc%2526utm_campaign%253Dapp-null-null-gpn_jp-cpc-pf-google-jp_cons%2526utm_content%253DBQ34Z100-R2%2526ds_k%253DBQ34Z100-R2%2526DCM%253Dyes%2526gclid%253DEAIaIQobChMIqdC9oaac_wIVEFhgCh24yQU3EAAYASAAEgJr__D_BwE%2526gclsrc%253Daw.ds), this is a newer chip that is compatible with the BQSTUDIO software, is compatible with the selected lead-acid battery and has an available, and still being manufactured, [evaluation](https://www.ti.com/tool/BQ34Z100EVM) board. The other option for our particular application is to change the chemistry of our selected battery. We are currently running on a lead-acid battery supply that results in our using older chips manufactured by Texas Instruments and, therefore, older evaluation boards and software making the overall process more difficult. If we were to switch the battery chemistry to a lithium-ion or lithium-polymer such as the [battery](https://www.jaycar.co.nz/12-8v-7ah-lithium-deep-cycle-battery/p/SB2210)[option](https://www.jaycar.co.nz/12-8v-7ah-lithium-deep-cycle-battery/p/SB2210), this would allow us to select a newly manufactured [battery fuel gauge chip](https://www.ti.com/lit/ds/symlink/bq28z620.pdf?ts=1685452445347&ref_url=https%253A%252F%252Fwww.ti.com%252Fpower-management%252Fbattery-management%252Fproducts.html). Selecting a newly manufactured chip gives us the advantage of better assistance from Texas Instruments on the functionality of the chip and allows us to use a new [evaluation board](https://www.ti.com/tool/BQ28Z620EVM-071) that is easier to use and compatible with the newest version of BQSTUDIO.

---

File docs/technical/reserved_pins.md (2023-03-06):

# Reserved pins on the ESP32

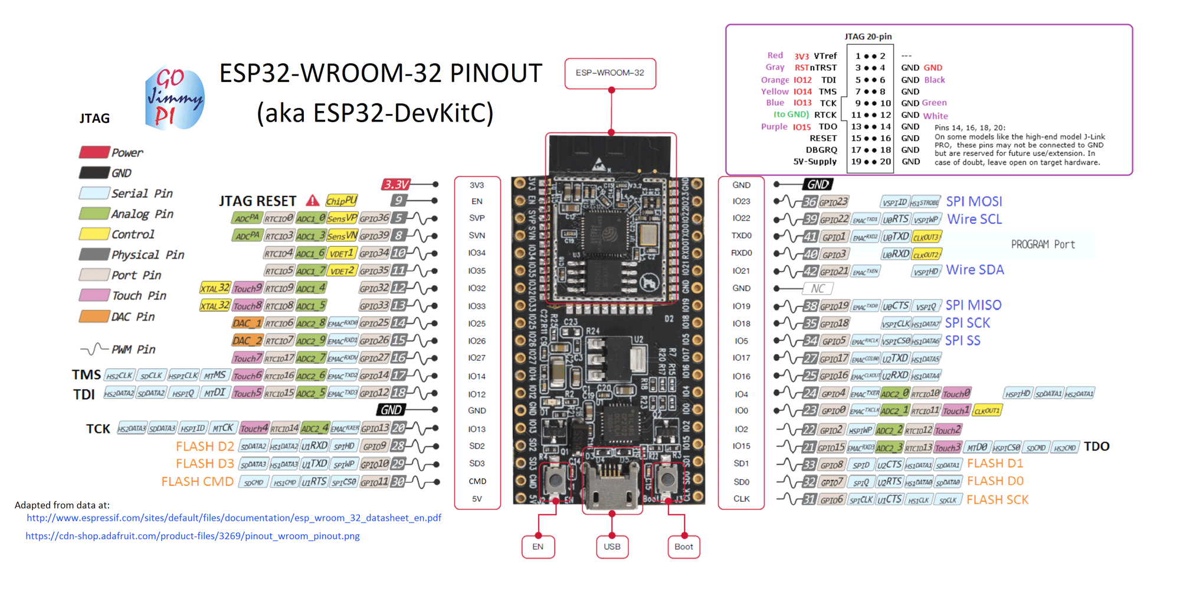
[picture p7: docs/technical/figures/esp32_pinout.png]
esp32 pinout


The following tables provides the GPIO number, pin number, pinout name, use, and additional notes about each GPIO pin.

- If the  *Used for* column is empty, the pin has not yet been reserved.
- The *Alt* column indicates any alternative GPIO pins for the current use.

This should only be filled in if the pin is currently reserved.
If any non-reserved pin can be used it will say *any*, and if no other pins can be used it will say *none*.

Source for some of the pins: <https://randomnerdtutorials.com/esp32-pinout-reference-gpios/>. There is more information here, so it is worth looking at before adding a new component.\*

The accessible pins on the DevKitC are: 0, 1, 2, 3, 4, 5, 6, 7, 8, 9, 10, 11, 12, 13, 14, 15, 16, 17, 18, 19, 21, 22, 23, 25, 26, 27, 32, 33, 34, 35, 36, and 39.

## System

These pins are reserved by the ESP32.
It is not possible to use these pins for anything else.

| GPIO Number | Pin Number | Name | Used for | Alt  | Special Functions | Notes |
| ----------- | ---------- | ---- | -------- | ---- | ----------------- | ----- |
| 1           | 41         | TXD0 | USB      | none | TX                | UART0 |
| 3           | 40         | RXD0 | USB      | none | RX                | UART0 |
| 6           | 31         | CLK  | Flash    | none |                   |       |
| 7           | 32         | SD0  | Flash    | none |                   |       |
| 8           | 33         | SD1  | Flash    | none |                   |       |
| 9           | 28         | SD2  | Flash    | none |                   |       |
| 10          | 29         | SD3  | Flash    | none |                   |       |
| 11          | 30         | CMD  | Flash    | none |                   |       |
| 16          | 25         | IO16 | SPIRAM   | none | RX                | UART2 |
| 17          | 27         | IO17 | SPIRAM   | none | TX                | UART2 |

## Base Board

| GPIO Number | Pin Number | Name | Used for      | Alt                    | Special Functions | Notes                                                    |
| ----------- | ---------- | ---- | ------------- | ---------------------- | ----------------- | -------------------------------------------------------- |
| 0           | 23         | IO0  | LED - G       |                        | ADC, RTC          | Outputs PWM on boot.                                     |
| 2           | 22         | IO2  | LED - R       | any                    | ADC, RTC, SPI     | Using UART1.                                             |
| 4           | 24         | IO4  | (LED - B)     | any                    | ADC, RTC, SPI     |                                                          |
| 5           | 34         | IO5  | SD - CS       | 15                     | SPI               |                                                          |
| 14          | 17         | IO14 | WiFi - EN     | any                    | ADC, RTC, SPI     | Outputs PWM on boot. Wakes wireless comms.               |
| 15          | 21         | IO15 | Battery - EN  |                        | ADC, RTC, SPI     | Outputs PWM on boot.                                     |
| 18          | 35         | IO18 | SD - CLK      | 14                     | SPI               |                                                          |
| 19          | 38         | IO19 | SD - DO       | 12                     | SPI               |                                                          |
| 23          | 36         | IO23 | SD - DI       | 13                     | SPI               |                                                          |
| 25          | 14         | IO25 | Battery - DAC | 26                     | DAC, ADC, RTC     | DAC to calibrate battery.                                |
| 26          | 15         | IO26 | Modem - Tx    |                        | DAC, ADC, RTC     |                                                          |
| 27          | 16         | IO27 | Modem - EN    | any                    | ADC, RTC          | Enable battery.                                          |
| 32          | 12         | IO32 | (Rain gauge)  | any (output capable)   | ADC, RTC          | Input 1. Use internal pull up                            |
| 33          | 13         | IO33 | (Rain gauge)  | any (output capable)   | ADC, RTC          | Input 2. Use internal pull up                            |
| 34          | 10         | IO34 | (Reserved)    |                        | ADC, RTC          | Input only. Reserved for future use.                     |
| 35          | 11         | IO35 | Modem Rx      | any (pref. input only) | ADC, RTC          | Input only. Using UART1.                                 |
| 36          | 5          | SVP  | Battery - ADC | 34, 35, 39             | ADC, RTC          | Input only. Read battery voltage. Needs 0.1uF capacitor. |

Items in brackets indicate that they may not be in use on the base board, so can be used on expansion boards.
In the case of *LED - B*, the pin may be freed up if deemed to not be necessary.
These pins may be used for something in future revisions, so expansion boards using these pins may not be compatible with newer base boards.

## Expansion Boards

The following table contains a template for expansion boards.

| GPIO Number | Pin Number | Name | Used for | Alt | Special Functions | Notes                     |
| ----------- | ---------- | ---- | -------- | --- | ----------------- | ------------------------- |
| 12          | 18         | IO12 |          |     | ADC, RTC, SPI     | Do not pull high on boot. |
| 13          | 20         | IO13 |          |     | ADC, RTC, SPI     |                           |
| 21          | 42         | IO21 |          |     | I2C               |                           |
| 22          | 39         | IO22 |          |     | I2C               |                           |
| 39          | 8          | SVN  |          |     | ADC, RTC          | Input only                |

It is possible to use I2C on pins 21 and 22, and UART or SPI can be used with an IO MUX to redirect the driver to one of the 5 pins.
Up to two SPI devices can be connected.

### SDI-Expansion

| GPIO Number | Pin Number | Name | Used for   | Alt | Special Functions | Notes                     |
| ----------- | ---------- | ---- | ---------- | --- | ----------------- | ------------------------- |
| 12          | 18         | IO12 | SDI - EN   | any | ADC, RTC, SPI     | Do not pull high on boot. |
| 13          | 20         | IO13 | SDI - FOut | any | ADC, RTC, SPI     |                           |
| 21          | 42         | IO21 | SDI - Dir  | any | I2C               |                           |
| 22          | 39         | IO22 | SDI - Tx   | any | I2C               |                           |
| 39          | 8          | SVN  | SDI - Rx   | any | ADC, RTC          | Input only                |

**Note:** when calling a pin in code, use the GPIO number, e.g. `machine.Pin(gpio_num, Pin.IN)`

- All output pins can be used for PWM.
- Any pins that output PWM on boot will remain high until set low.
- Input only pins do not have internal pull-up/pull-down resistors.
- All other pins are low on boot.
- The max current draw per GPIO is 40mA.
- All GPIO pins can be configured as interrupts.
- ADC pins are 12-bit analog to digital converters.
- DAC pins are 8-bit digital to analog converters.
- RTC pins can be used in deep sleep with the ULP.
- The RTC numbering is different from the GPIO numbering.

---

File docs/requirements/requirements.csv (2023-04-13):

Environmental Monitoring IoT Project Requirements / Wish-list
Hardware | Raised by | Comments (Please initial comments and add extra columns as necessary)
Low-powered | DT
Accurate clock management | DT
Quality time chip sync'd with reliable time server | DT
All data time-stamped to NZ Standard time (UTC +12) | DT
Time-stamp to nearest second | DT
Rechargeable battery pack - 'hot-swapable' | DT
Data logged to micro SD card | DT
Wireless comms to programming interface - iOS device. Bluetooth / Wifi? (activated by switch/magnet to save power?) | DT
Comms via Vodafone NB-IoT Band 28 | DT | Potential for Spark IoT later? i've also heard of cubesat's being used-EC
Weatherproof / Waterproof. Glands / connectors? Hydrophobic vent? Potting of electronics? | DT
External antenna connection (SMA) | DT
USB port for programming device / diagnositics? | DT
Robust data transfer protocol to ensure no data loss (data pointers? transfer file numbering?) | DT
Appropriate design for mounting within Raingauges (TB3, Rimco) as well as in huts and for stand alone applications | EC
SDI-12 Variant
SDI-12 serial communcations protocol (USGS) | DT
Relay for powering up attached smart sensor (12v) or voltage output to activate external relay. | DT
Pulse input Variant
Ability to monitor 1 'pulse' input (preferably 2?) - monitor normally open reed switch closure | DT
De-bounce on pulse input. Resistor / Capacitor circuit. Selectable on/off? | DT
Software - Local Interface | Raised by | Comments
iOS app for device configuration | DT
configure basic settings through the app such as sensor set-up: | DT
* clock setting | DT
* comms settings (network connections and data transfer interval) | DT
SDI-12 Variant
* recording interval | DT
* request 'live' reading from SDI-12 sensor | DT
* set offset (zero) to recorded value | DT
* set calibration multiplier (span)? | DT
* SDI-12 commands (pre programed commands?) | EC | eg change address, measure commands- EC
* Calibration/validation mode (prevent logging erroneous values while on site) | EC
Pulse input Variant
* set calibration multiplier | DT
* view accumulated totaliser | DT
* 'zero' accumulated totaliser | DT
* Validation mode (prevent logging validation/test tips) | EC
Software - Server | Raised by | Comments
Flexible data storage format - allowing future integration with GWRC databases / applications | DT
Robust data transfer protocol to ensure no data loss (data pointers? transfer file numbering?) | DT
Explore possibility of also enabling transfer of data to FTP server using existing supplierss custom XML data format. | DT
View data in tabular and graph format, identify missing data, identify comms failure. | DT
Retrieve / send device settings from server? | DT
Set trigger levels on different data sets - send email and or SMS to contact list (Twilio or other HTTP messaging service?) | DT
Send email / sms based on missing data, comms failure, system issues | DT

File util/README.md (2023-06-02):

# Util Directory

Contents of this directory:

- `micropython-software` - micropython tests ran under docker. High level business logic code - nothing hardware specific.
- `micropython-hitl` - hardware-in-the-loop tests. In CI, ran by a custom runner that has a devkit attached.
  - `pyboard.py` standalone micropython tool. [Documentation](https://docs.micropython.org/en/latest/reference/pyboard.py.html). Used to run code on the devices
- `scripts`:
  - `commit-lint.sh` - commit message linter (deprecated - using gitlint)

## CI/CD (DevOps) Overview

A big part of DevOps is Continuous Integration and Continuous Delivery, collectively sometimes referred to as CI/CD.

Continuous Integration (CI) is the practice of automating the integration of code changes through compilation, static analysis and testing.
Meanwhile, Continuous Delivery (CD) is a development approach that prioritises short software release cycles, in an effort to build and release software at a greater speed and accuracy while also reducing cost, time and risks.

We make use of DevOps practices such as CI/CD to reinforce the Agile software development methodology employed in the project, and to ensure consistently high quality software was being written.
In particular, Hardware-in-the-loop testing was built to run automated code tests on real world hardware.
Linting tools are used to enforce a standard code-writing style, and CD pipelines allow automated typesetting and delivery of updated academic reports.
This section briefly discusses the rationale, design and implementation of these techniques.

## Docker-Based Testing

A _Dockerfile_ was built to install the Micropython Unix port into a Docker Image.
This image was uploaded to the ECS GitLab.
_GitLab CI/CD_ has the ability to use Docker images as the basis for running automated pipelines.
When a new CI job is created from a git push or branch merge, it creates a container from the uploaded Micropython image, setting the entrypoint of the container to run the test suite from the device code.

The benefits of this approach is that the high level logic of the embedded software could be evaluated and tested quickly.
With no resource constraints (in comparison to the devices), the scripts could run quickly and hence feed back timely information to the developers.

However, the speed benefits come at a cost of flexibility.
The Unix port implements a subset of the Micropython standard library, so some functions, especially hardware-specific or low-level, do not work.
Furthermore, resource constraints (such as low available RAM, clock speed) do not exist, so it is hard to get a realistic estimate of how the code would perform on the embedded device.
As a result, the docker-based tests are useful for testing high level code and algorithms.

## Hardware-In-The-Loop (HITL) testing

HITL tests were designed to address the limitations of docker-based software tests mentioned above.
HITL uses a custom GitLab Runner on a Raspberry Pi connected to an ESP32 dev-kit over USB.
A script was written that compiles and uploads the latest code to the dev-kit, runs the HITL tests included in the compiled code, and returns an exit code based on the results.
See [HITL Readme](micropython-hitl/README.md) for a technical overview of how HITL tests run.

The benefits of this approach is that code runs _directly on the hardware we are using in the project_.
If a test fails here, it is extremely likely to fail in the field.
HITL tests enable a high sense of confidence in writing high quality low-level code.
This is especially important for hardware drivers, discussed in the Hardware Report.

The downsides of HITL testing is speed - it takes longer to run the HITL tests than it does on docker, so the number of HITL based tests should be minimised, instead focussing on useful, hardware-centric tests.
Testing software components, especially high-level code, should remain in the docker test suite.
Another downside of HITL testing is that jobs can't be run in parallel - while not a problem right now, in the future jobs could get queued up, slowing down the CI pipelines as the ESP32 can only run one test at a time.
We could get around this if we bought multiple ESP32s to plug into the gitlab runner machine, although this could get complicated and unreliable trying to manage lots of serial devices.

Unfortunately, the serial connection to the ESP32 was fairly unstable and due to time constraints, HITL tests were temporarily disabled.
We plan on re-enabling the HITL tests later in the year - probably around iteration 2, when we will focus on building the first prototype device.

## Linting and Static Analysis

Static Analysis is a method of inspecting code without running the program.
In our project, we use Black for linting code, and a custom bash script for linting Git commit messages.

Black, the uncompromising code formatter' forces developers to cede control over the formatting of python code.
It's deterministic and strict linting rules are enforced through Gitlab CI, preventing poor style from being committed to the master code branch.
Code is formatted as it is written using pre-commit hooks.

Black was compared against other formatting tools, such as Flake8 and Pylint.
While all do a good job of linting code against the standard PEP8, Black enforces the code style extremely strictly, and its auto-formatting tools allows us to focus on writing code, rather than manually fixing the errors.

Git commit messages are checked by [gitlint](https://jorisroovers.com/gitlint/) which enforces a modified Angular Commit style.
The benefit of this is that it is easy to see at a glance the scope, type and changes of a commit.
As a result, reviews, debugging and auditing code changes are more accessible and faster to perform.

## CD: LaTeX Report Typesetting

Gitlab CI automatically typesets the academic LaTeX reports, and stores the output as a build artifact from the Job.
It does this using a custom Docker image that works similarly to the Docker tests described above.
The image contains all the necessary scripts and style files required to build the reports.
The primary benefit of CI-based typesetting is that the client, project supervisor and team members can always read the latest compiled version of a report for review.
This comes at a small performance decrease - the LaTeX files are always built, regardless of the commit type - but they only take a matter of seconds to build, so are considered acceptable.

## Discord Bot

This is a copy of a dicord bot that we have been using to send our message-logs from discord to mattermost. It is saved as discord_bot.py

It takes the messages from the discord server it was added to, and accesses the users Discord nick-name(Set name in the discord server) and sends the message to mattermost under that name followed by "- Discord".

The benifits of utilizing this software are as follows: The communication is done on a platfrom that is more comfortable for the developers; as a result of this the use of the tool is far more consistent, and the developers are more engaged in the project.

However the benifits of using discord come with the costs of using this as opposed to pure mattermost. These are as follows: The features and tools that make mattermost an appealing choice are not accessible from discord; The links to issues, aswell as the ability to create issues from mattermost are not replicable in discord. There are gaps in communication; There are gaps in the messages on discord where issues are discussed with stake-holders on mattermost. This leads to a discrepency in recorded communication.

Despite these drawbacks the sheer frequency of engagement is so much greater due to the use of this bot that it over-rides any disadvantages listed above when using this in a 300 level environment. If we compare the engagement in the hard-ware mattermost channel to the web or embedded teams that were utilizing this mattermost bot, it is clear to see that the trade-offs are worth taking.

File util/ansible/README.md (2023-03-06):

# HTLPi Build & Test Server

The configuration is specified as an Ansible playbook.

The current device name is `HTL` which was specified manually by `raspi-config`. Should find a way to do this via a command.

## Files

The files in this directory are the files which would have to be created/copied when a fresh version of the build & test server is provisioned.

### WiFi Configuration

The `wpa_supplicant.conf` file specifies the connection to the `WellingtonUniversityGuest` WiFi access point. The current Raspberry Pi 3B+ hardware was whitelisted by Mark Davies. Future devices should added to the MyDevices portal <https://mydevices.wgtn.ac.nz/> (staff login required).

The current WiFi network status is:

```shell
pi@HTL:~ $ wpa_cli -i wlan0 status
bssid=ac:4a:56:c2:d6:a3
freq=2462
ssid=WellingtonUniversityGuest
id=0
mode=station
pairwise_cipher=NONE
group_cipher=NONE
key_mgmt=NONE
wpa_state=COMPLETED
ip_address=10.140.153.132
p2p_device_address=02:c4:dc:2d:e0:be
address=b8:27:eb:8f:6c:96
uuid=55201e7d-f982-5977-b32c-ee53f10046d5
```

### Bash

The file [bashrc](files/bashrc) has some small additions to the defaults for making the Bash history easier to work with:

```shell
pi@HTL:~ $ diff .bashrc .bashrc~
19,22c19,20
< HISTSIZE=2000
< HISTFILESIZE=8000
< HISTTIMEFORMAT="%F %T "       # Timestamp.
< PROMPT_COMMAND="history -a"   # Write to HISTIFLE immediately
---
> HISTSIZE=1000
> HISTFILESIZE=2000
```

### gitlab-runner

It appears that `gitlab-runner` on Debian OS's create a new user `gitlab-runner` and the runner is installed and runs on the system, rather than in the user space as on macOS. The `config.toml` file is thus stored in `/etc/gitlab-runner/config.toml` and is readable only by `root`:

```shell
pi@HTL:~ $ sudo ls -al /etc/gitlab-runner/
total 12
drwx------   2 root root 4096 Jul 27  2020 .
drwxr-xr-x 116 root root 4096 Nov 11 14:17 ..
-rw-------   1 root root  297 Jul 27  2020 config.toml
```

### ssh

The file `sshd_config` disables password authentication and allows public key authentication and needs to be copied to `/etc/ssh`. The host keys also potentially need to be part of the provisioning of the build & test server but will need to be stored securely in the repo. The contents of `/etc/ssh/` are:

```shell
pi@HTL:~ $ sudo ls -l /etc/ssh/
total 584
-rw-r--r-- 1 root root 553122 Mar  2  2018 moduli
-rw-r--r-- 1 root root   1723 Mar  2  2018 ssh_config
-rw-r--r-- 1 root root   3296 Apr 21  2021 sshd_config
-rw------- 1 root root    672 Mar 14  2018 ssh_host_dsa_key
-rw-r--r-- 1 root root    606 Mar 14  2018 ssh_host_dsa_key.pub
-rw------- 1 root root    227 Mar 14  2018 ssh_host_ecdsa_key
-rw-r--r-- 1 root root    178 Mar 14  2018 ssh_host_ecdsa_key.pub
-rw------- 1 root root    411 Mar 14  2018 ssh_host_ed25519_key
-rw-r--r-- 1 root root     98 Mar 14  2018 ssh_host_ed25519_key.pub
-rw------- 1 root root   1675 Mar 14  2018 ssh_host_rsa_key
-rw-r--r-- 1 root root    398 Mar 14  2018 ssh_host_rsa_key.pub`
```

---

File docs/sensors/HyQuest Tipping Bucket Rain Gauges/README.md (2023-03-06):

# HyQuest Tipping Bucket Rain Gauges

We received a TB6/0.2mm rain gauge for development and evaluation, but HyQuest also produce other models which are used by Regional Councils. The PDFs in this directory were downloaded from HyQuest's product pages:

- <https://www.hyquestsolutions.com.au/products/hardware/meteorology/tb6-series-ii-tipping-bucket-rain-gauge>
- <https://www.hyquestsolutions.com.au/products/hardware/meteorology/tb3-tipping-bucket-rain-gauge/>

---

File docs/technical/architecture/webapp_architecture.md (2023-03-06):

# Web App Architecture

- [Web App Architecture](#web-app-architecture)
  - [Build Process](#build-process)
  - [Implementation of Architecture using Functional Components](#implementation-of-architecture-using-functional-components)
  - [Handling "Globally" Shared resources](#handling-globally-shared-resources)
  - [Implementation of User-feedback Notifications](#implementation-of-user-feedback-notifications)

The Web App is the primary way of configuring the device and calibrating the sensor readings.
This section discusses the architecture, build process and functional implementation of the frontend, built on the Preact framework.
For an outline of the requirements and decisions that went into the _web design_, see the [2020 Software Report](/docs/literature/Secker2020FinalReport.pdf).

At a high level, the _App_ component is the Web App entrypoint and top-most component, being rendered first by the browser
Once the entire pre-rendered static files have been loaded by the client, the app makes requests to the backend API endpoints `/config` and `/data`
These endpoints return JSON objects which represent the state of the entire application
The _App_ component passes the relevant information as "props" - read-only arbitrary inputs - to its child components
Each subcomponent contains code to render a UI component based on its internal state and its props.

<!-- TODO: Put in a DAG-style dependency graph -->

## Build Process

To turn the Web App source files and dependencies into a
production-ready Web App running on the microcontroller, an optimised
build process was configured.

The first stage in the build process checks for typescript errors.
[Typescript](https://www.typescriptlang.org/) is an extension to Javascript that adds static typing.
We explicitly enforce strict static typing for the entire project - every variable needs an explicitly defined type (or infers it).
For example, a portion of the global `interfaces.ts` file defines the types associated with the data returned by the backend API, shown in the following listing:

```typescript
export type SDISensorType = { address: string; bootup_time: number; enabled: boolean }
const sensor: SDISensorType = { address: 'A', bootup_time: 1, enabled: true }
```

In this example, the type `SDISensorType` concretely implements part of the device configuration defined [here](configuration.md).
This allows the programmer to create a new object, _sensor_, that implements this interface.
Defining this type enforces the primitive types (strings, numbers, booleans etc) of the properties of a sensor object, leading to less type errors, more resilient code and reducing development time.

The second stage _transpiles_ React code into native Javascript.
Transpiling is the process performed by the library [Babel](https://babeljs.io/) that allows modern code to be backwards compatible and support all browsers.
This process also involves injecting environment variables into the code.
Environment variables are used by the developer and Continuous Integration process  to differentiate between a development and production build.
In a development build, the Web App connects to a [webserver simulator backend](/software/simulator/src/README.md), whilst a production build uses the webserver on the microcontroller.
Environment variables enable this switch between contexts.

The third stage, performed by the [WebPack](https://webpack.js.org/) library, minifies and bundles the transpiled code into HTML, CSS and Javascript files.
Minification is a process that removes unnecessary or redundant data from the source code without changing the functionality - things like shortening variable names, removing formatting and comments, etc.
A further optimisation we perform on top of the webpack process is to compress the bundled files with _gzip_.
This has the effect of reducing the total file-size by around 50%.
This is performed in the [build.sh script](/software/device/build.sh).

## Implementation of Architecture using Functional Components

The structure of each component in the Web App follows a functional paradigm, where components are composed from literal javascript functions, for example:

```typescript
    const component: FunctionalComponent = (props: PropType) => {
        return <div>I am a component named {props.name}!</div>
    }
```

This design allows for strong composability and makes it easy to reason about the state of the component.
An interesting note is that the code above is not valid javascript - the return statement returns HTML directly.
This is a react-specific syntactic extension of javascript called JSX, that combines javascript and HTML into the same file.
Because the browser does not natively understand JSX, part of the compilation process "transpiles" this code into browser-readable javascript, as described above.

The ideal functional component is _"pure"_, containing no side effects or mutable state.
However, in a dynamic Web Application the state changes often - buttons are pressed, dropdowns toggled, and forms are modified.
This is accomplished in functional components with [React Hooks](https://reactjs.org/docs/hooks-intro.html), a feature of the React framework.
Hooks are a new feature of the library that offer ways to "attach" reusable behaviour to a component.

One such hook is the `useState()` hook.
These hooks allow reuse of state logic without changing the component hierarchy, letting components change their output over time in response to user actions, network responses and anything else without violating the functional rule.
For example, the _Monitor_ component needs to track mutable state to store whether or not it can send commands to the device.
This can be stored in the component with `const [canSend, setCanSend] = React.useState(true);` In this line, `useState(true)` declares a "state variable" with a default value of `true`.
The function returns a pair of variables - `canSend` represents the state, and `setCanSend` is a reference to a callback function used to mutate the state.

This pattern is used throughout the application almost every component
It has allowed for simpler code that is easier to reason about and debug, and the functional design matches the design decisions of the device software.

## Handling "Globally" Shared resources

One problem faced with the architecture of the Web Application is globally-accessible state.
Most of the dynamic data in the application comes from the top layer _App_ component, which calls the backend API and passes the device data as props to subcomponents.
This relation is one-way, and props are read-only.
What happens if a sub-component, such as one that updates the device configuration, wants to update the top-level config object, so that the page doesn't have to be refreshed every time the onfiguration changes?
To ensure two-way communication back to the top component, the top-layer _update API_ method would need to be passed down to every component through props, leading to the well known and hard-to-maintain "callback hell".

To get around this problem, react provides another type of hook - `useContext()`.
A _context_ is an object with two values - a Provider and a Consumer, created with a library function `createContext()`.
the `useContext()` hook takes a context as an argument and returns the _context value_ for that context.
The value is determined by a specific prop - `value` - from the first Provider that sits above the the calling component in the tree.

In our app, we wrap the top layer `App` component in a context Provider, passing the `fetchConfig()` method - the method that retrieves the latest config from the webserver - into the provider as the _value_ argument.
Subcomponents that want to use the context now only have to call `useContext(fetchApiContext)`, which returns the callback function that updates the configuration data.
Now, every sub-component can be responsible for refreshing the applications global state.

## Implementation of User-feedback Notifications

The library [Notyf](https://www.npmjs.com/package/notyf) is used to implement notifications that display informational, success and error messages to the user. Notifications were implemented to provide a standard way of giving feedback to actions that hit the backend API in a centralised place. Furthermore, because API calls often took multiple seconds to run on the microcontroller, a message-based system helps assure the user that _something_ is happening.

Global notifications were implemented using the same `useContext()` hooks discussed earlier. An interesting issue was that the library caused the compiler to throw errors in the production build process, halting the compilation. This is because the library relies on the DOM, which is only available in the browser. Pre-rendering runs in Node, which has no access to browser APIs. To get around this, a mock Notyf context was implemented that overrides the notification methods with empty stubs. A higher-order function was implemented to wrap the `useContext()` method, returning the actual Notyf context if the DOM is accessible, or the mock context otherwise.

Relevant code: [`software/device/webapp/src/util/notyfContext.ts`](/software/device/webapp/src/util/notyfContext.ts)

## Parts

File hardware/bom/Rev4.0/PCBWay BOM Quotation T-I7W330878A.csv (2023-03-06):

PCBWay Bom Quotation, Product No.:T-I7W330878A
Item # | *Designator | *Qty | Manufacturer | *Mfg Part # | Description / Value | *Package/Footprint | Your Instructions / Notes | *Unit Price(5 sets) | *Total | *Delivery Time | *Actual Purchase Mfg Part # | *PCBWay Note | Customer Reply | PCBWay Update
1 | C100,C102,C106,C305,C307,C308,C502 | 7 | Yageo | CC0603KRX5R8BB104 | 100nF | OPL_Capacitor:C0603 |  | $0.240 | $8.400
2 | C101,C103,C104,C105,C302,C303,C501 | 7 | Yageo | CC0805KKX5R8BB106 | 10uF | OPL_Capacitor:C0805 |  | $0.080 | $2.800
3 | C200 | 1 | Yageo | CC0603KRX7R8BB332 | 3.3nF | OPL_Capacitor:C0603 |  | $0.160 | $0.800
4 | C201,C204,C402,C403,C404 | 5 | Yageo | CC0603KRX5R8BB104 | 100nF | OPL_Capacitor:C0603 |  | $0.240 | $6.000
5 | C202 | 1 | Yageo | CC0603KRX6S8BB105 | 1uF | OPL_Capacitor:C0603 |  | $0.240 | $1.200
6 | C203,C205,C304 | 3 | Yageo | CC0603KRX5R8BB104 | 100nF | OPL_Capacitor:C0603 |  | $0.240 | $3.600
7 | C300,C301,C306,C309,C310 | 5 | Yageo | CC0805MKX5R8BB226 | 22uF | OPL_Capacitor:C0805 |  | $0.480 | $12.000
8 | C311,C503 | 2 | Yageo | CC0603KRX5R8BB104 | 100uF | OPL_Capacitor:C0603 |  | $0.240 | $2.400
9 | C400 | 1 | Yageo | CC0603KRX5R8BB104 | 100nF | OPL_Capacitor:C0603 |  | $0.240 | $1.200
10 | C500 | 1 | Yageo | CC0805MKX5R8BB226 | 22uF | OPL_Capacitor:C0805 |  | $0.480 | $2.400
11 | D100 | 1 | Diodes Incorporated | 1N5819HW1-7-F | 1N5819HW1-7-F | Diode_SMD:D_SMA |  | $0.407 | $2.035
12 | D101 | 1 | Kingbright | APTF1616SEEZGQBDC | RGBLED |  |  | $0.708 | $3.540
13 | D200 | 1 | Diodes Incorporated | BZT52C5V6T-7 | BZT52C5V6T-7 |  |  | $0.272 | $1.360 | 7-10 Workdays
14 | D300 | 1 | Diodes Incorporated | 1N5819HW1-7-F | 1N5819HW1-7-F | Diode_SMD:D_SMA |  | $0.407 | $2.035
15 | D301 | 1 |  | 19-217-R6C-AL1M2VY-3T | RED_LED | LED_SMD:LED_0603_1608Metric | Put any Red led that match the footprint | $0.452 | $2.260
16 | D302 | 1 | Toshiba Semiconductor and Storage | CRS08 | CRS08 | SODFL3500X98N |  | $0.708 | $3.540
17 | D303 | 1 | Diodes Incorporated | 1N5819HW1-7-F | 1N5819HW1-7-F | Diode_SMD:D_SMA |  | $0.407 | $2.035
18 | IC200 | 1 | Texas Instruments | BQ34Z110PWR | BQ34Z110PWR | SOP65P640X120-14N |  | $9.072 | $45.360 | 7-10 Workdays
19 | J100 | 1 | Molex | 1050170001 | USB_B_Micro | CON_1050170001 |  | $0.407 | $2.035
20 | J102 | 1 | GCT | MEM2075-00-140-01-A | SDCARD |  |  | $2.631 | $13.155 | 7-10 Workdays
21 | J103 | 1 |  | NPTC041KFXC-RC | I2C |  |  | $0.708 | $3.540
22 | J104 | 1 |  | NPTC041KFXC-RC | WIFI_EN |  |  | $0.708 | $3.540
23 | J105 | 1 | Molex | 878980826 | MODEM_A |  | Connector | $2.470 | $12.350 | 7-10 Workdays | 87898-0826
24 | J106 | 1 | Molex | 878980826 | MODEM_B |  | Connector | $2.470 | $12.350 | 7-10 Workdays | 87898-0826
25 | J300 | 1 | W黵th Elektronik | 691508110302 | BATT |  | Connector | $4.793 | $23.965 | 7-10 Workdays | 691709710302
26 | J400 | 1 | W黵th Elektronik | 691508110302 | Grain_gauge |  | Connector | $4.793 | $23.965 | 7-10 Workdays | 691709710302
27 | J500 | 1 | W黵th Elektronik | 691508110304 | SDI-12 |  | Connector | $5.040 | $25.200
28 | L300,L301 | 2 | Bourns Inc. | SRN5040-4R7M | 4.7uH | SRN5040-4R7M:INDPM5050X400N |  | $0.484 | $4.840
29 | MH100,MH101,MH103 | 3 |  | M3 | ${TOPCODE} |  | Though holes |  |  |  |  | [DNP];
30 | Q100 | 1 | Diodes Incorporated | BC847A-7-F | BC847 | Package_TO_SOT_SMD:SOT-23 |  | $0.407 | $2.035
31 | Q101 | 1 | Diodes Incorporated | BC847A-7-F | BC847 | Package_TO_SOT_SMD:SOT-23 |  | $0.407 | $2.035
32 | Q200 | 1 | ON Semiconductor | 2N7002NCT-ND | 2N7002 | Package_TO_SOT_SMD:SOT-23 |  | $0.126 | $0.630 |  | 2N7002 | The part we will supply is made by Slkor
33 | Q201 | 1 | ON Semiconductor | BSS84CT-ND | BSS84 | Package_TO_SOT_SMD:SOT-23 |  | $0.138 | $0.690 |  | BSS84 | The part we will supply is made by Slkor
34 | Q202 | 1 | ON Semiconductor | 2N7002NCT-ND | 2N7002 | Package_TO_SOT_SMD:SOT-23 |  | $0.126 | $0.630 |  | 2N7002 | The part we will supply is made by Slkor
35 | Q300 | 1 | ON Semiconductor | FDN360P | FDN360P | OPL_Discrete_Semiconductor:SOT-23 |  | $1.248 | $6.240
36 | Q301 | 1 | ON Semiconductor | FDN360P | FDN360P | OPL_Discrete_Semiconductor:SOT-23 |  | $1.248 | $6.240
37 | Q500 | 1 | ON Semiconductor | FDN360P | FDN360P | OPL_Discrete_Semiconductor:SOT-23 |  | $1.248 | $6.240
38 | Q501 | 1 | ON Semiconductor | FDN361BN | FDN361BN | OPL_Discrete_Semiconductor:SOT-23 |  | $0.720 | $3.600 | 15 Workdays
39 | Q502 | 1 | ON Semiconductor | FDN361BN | FDN361BN | OPL_Discrete_Semiconductor:SOT-23 |  | $0.720 | $3.600 | 15 Workdays
40 | R100,R306 | 2 | Yageo | RC0603FR-0710KL | 10K | OPL_Resistor:R0603 |  | $0.011 | $0.110
41 | R101,R102 | 2 | Yageo | RC0603FR-07470RL | 470 | OPL_Resistor:R0603 |  | $0.016 | $0.160
42 | R103,R104 | 2 | Yageo | RC0603FR-0710KL | 10K | OPL_Resistor:R0603 |  | $0.011 | $0.110
43 | R105,R204,R205,R301,R305,R400,R401,R402,R403,R404 | 10 | Yageo | RC0603FR-0710KL | 10K | OPL_Resistor:R0603 |  | $0.011 | $0.550
44 | R106,R107 | 2 | Yageo | RC0603FR-07100RL | 100 | OPL_Resistor:R0603 |  | $0.013 | $0.130
45 | R200 | 1 | Yageo | RC0603FR-10100KL | 100K | OPL_Resistor:R0603 |  | $0.088 | $0.440
46 | R201 | 1 | Yageo | RC0603FR-07165KL | 165K | OPL_Resistor:R0603 |  | $0.088 | $0.440
47 | R202 | 1 | Yageo | RC0603FR-07300KL | 300K | OPL_Resistor:R0603 |  | $0.033 | $0.165
48 | R203 | 1 | Yageo | RC0603DR-0716K5L | 16K5 | OPL_Resistor:R0603 |  | $0.088 | $0.440
49 | R206,R207,R208,R209,R212,R214 | 6 | Yageo | RC0603FR-07100RL | 100 | OPL_Resistor:R0603 |  | $0.013 | $0.390
50 | R210 | 1 | Yageo | RC0603FR-1010KL | 10K | OPL_Resistor:R0603 |  | $0.088 | $0.440
51 | R213 | 1 | Yageo | PE0805DRF7W0R1L | 0.1 | OPL_Resistor:R0805 |  | $1.000 | $5.000
52 | R300 | 1 | Yageo | RC0603FR-0756KL | 56K | OPL_Resistor:R0603 |  | $0.032 | $0.160
53 | R302 | 1 | Yageo | RC0805FR-073K3L | 3K3 | OPL_Resistor:R0805 |  | $0.055 | $0.275
54 | R303 | 1 | Yageo | RC0603FR-10100KL | 100K | OPL_Resistor:R0603 |  | $0.088 | $0.440
55 | R304 | 1 | Yageo | RC0603FR-0745K3L | 5K3 | OPL_Resistor:R0603 |  | $0.033 | $0.165
56 | R405 | 1 | Yageo | RC0603FR-074K7L | 4K7 | OPL_Resistor:R0603 |  | $0.028 | $0.140
57 | R500,R501,R502 | 3 | Yageo | RC0603JR-071ML | 1M | OPL_Resistor:R0603 |  | $0.007 | $0.105
58 | R503 | 1 | Yageo | RC0603JR-070RL | 0 | OPL_Resistor:R0603 |  | $0.021 | $0.105
59 | SP200 | 1 |  | * | ${TOPCODE} |  | Bridge |  |  |  |  | [DNP];
60 | SW100 | 1 | CIT Relay and Switch | CS11025.0F160 | Push_Button | OPL_Switch:SW4-SMD-6.0X6.0X5.0MM |  | $0.348 | $1.740 | 7-10 Workdays
61 | TP100,TP101,TP103 | 3 |  | RevPol | RevPol | Connector_Pin:Pin_D1.0mm_L10.0mm | Test point |  |  |  |  | [DNP];
62 | TP102,TP104,TP105,TP106,TP301,TP304 | 6 |  | RevPol | RevPol | Connector_Pin:Pin_D1.0mm_L10.0mm | Test point |  |  |  |  | [DNP];
63 | TP300 | 1 |  | 5V | 5V | Connector_Pin:Pin_D1.0mm_L10.0mm | Test point |  |  |  |  | [DNP];
64 | TP302 | 1 |  | 3V3 | 3V3 | Connector_Pin:Pin_D1.0mm_L10.0mm | Test point |  |  |  |  | [DNP];
65 | TP501 | 1 |  | SDI_Tx | SDI_Tx |  | Test point |  |  |  |  | [DNP];
66 | TP502 | 1 |  | SDI_Rx | SDI_Rx |  | Test point |  |  |  |  | [DNP];
67 | U100 | 1 | Silicon Labs | CP2104-F03-GM | CP2104 | Package_DFN_QFN:QFN-24-1EP_4x4mm_P0.5mm_EP2.6x2.6mm |  | $4.584 | $22.920
68 | U101 | 1 | Espressif Systems | ESP32-WROVER-B (8MB) | ESP32-WROVER-B | esp32-wrover:ESP32-WROVER |  | $9.480 | $47.400 |  |  | Price may increase after you place the order due to the worldwide components shortage. Plz confirm asap.Or you can supply this part to us for assembly
69 | U300 | 1 | Texas Instruments | TPS562201DDCR | TPS562201DDCR | Package_TO_SOT_SMD:SOT-23-6 |  | $1.085 | $5.425
70 | U301 | 1 | Texas Instruments | LM2831XMF | LM2831XMF | SOT95P280X145-5N |  | $3.240 | $16.200 |  | LM2831XMF/NOPB
71 | U400 | 1 | Texas Instruments | PCF8574ADGVR | PCF8574ADWR |  |  | $2.553 | $12.765 | 7-10 Workdays
72 | U401 | 1 | Nexperia USA Inc. | 74HC590D,118 | 74HC590D,118 | SOIC127P600X175-16N:SOIC127P600X175-16N |  | $0.801 | $4.005 | 7-10 Workdays
73 | U402 | 1 | Texas Instruments | LM393-N | LM393-N |  |  | $2.216 | $11.080 | 7-10 Workdays | LM393N/NOPB
74 | U500 | 1 | Texas Instruments | SN74LS00DR | SN74LS00DR | Package_SO:SOIC-14_3.9x8.7mm_P1.27mm |  | $0.816 | $4.080
75 | U501 | 1 | Texas Instruments | SN74LVC2G241DCUR | SN74LVC2G241DCUR | Package_SO:VSSOP-8_2.3x2mm_P0.5mm |  | $0.538 | $2.690
76 |  | 5 | Silicon Labs | SI7201-B-09-IB | Sensor, Hall effect |  | buy but not assembly | $2.168 | $54.200 | 7-10 Workdays
 |  |  |  |  |  |  |  | component price | $452.115
 |  |  |  |  |  |  |  | assembly price | $88.000
 |  |  |  |  |  |  |  | board price | $54.480

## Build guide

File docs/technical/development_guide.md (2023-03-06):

# Development Guide

Once you have the [hardware set up](hardware_setup.md), you have initialised your [dev environment](dev_environment_setup.md), and have uploaded [micropython to the board](micropython_build.md), these instructions show how to get started with development of the embedded software.

## Uploading Device Code

The [build script](/software/device/build.sh) compiles the embedded micropython code into `.mpy` files (frozen bytecode), and compiles the webapp code into minified/gzipped static files.

Running the build script with `./build.sh` generates a `build/` folder, which can be uploaded directly to the device.

This project predominantly uses `rshell` to interact with the device. `rshell` has an `rsync` function that syncronises a local folder with the device folder.

To sync the build folder and device, try:

```repl
rshell --port /dev/ttyXXX --baud 115200 rsync build/ /pyboard
```

***Development note:** If you are only changing a couple of files we recommend copying only the changed files using `cp` (rather than using `rsync`, which will take longer). For example if you made changes in `main.py` and `drivers/modem.py` you can:

```bash
rshell --port /dev/ttyS* -b 115200 cp src/main.py /pyboard
rshell --port /dev/ttyS* -b 115200 cp src/drivers/modem.py /pyboard/drivers
```

## Provisioning The Device

### Initial Device config

The device requires some configuration files, stored on the SD card, to run:

First, copy the example config:

```bash
cd software/device/embedded/src/services/
cp device-config.example.json device-config.json
```

Then, open the file and make some changes.

- `device_name`: Set a unique serial number in the device name - this will be used in setting the MQTT topic.
- `device_id`: Set to match the serial number in device_name
- `send_interval` interval: how often you want the device to send MQTT message.
- `symmetric_key`: MQTT client ID

After saving the config file, upload it to the device's SD card.

```bash
rshell --port /dev/ttyXXX --baud 115200 rsync provision /pyboard/sd/services
```

We have an incomplete [provision step](/software/device/embedded/src/provision.py) to generate this device config based on an interactive prompt.

### u-blox SARA-R4 Modem Registration

The modem needs to register with a network operator to obtain cellular network access. The data recorder registers with Vodafone by default. The manual steps for registration follow.

Open the REPL through rshell.

```shell
rshell --port /dev/ttyXXX -b 115200 repl
```

With the REPL open, run the following:

```python
import provision
provision.provision()
```

Type `modem` and hit enter.

The device will attempt to automatically register with the network operator for you. If successful, you should see a blue LED flashing on the SparkFun Shield which indicates the SARA-R4 modem has successfully registered with the network operator. Press enter to exit.

If you fail to provision the modem after serval attempts you should check the following:

1. Power: Is the SparkFun Shield's red LED lit?
1. SIM card: Do you have a SIM card with plan inserted to the modem?
1. Serial Communication: Is the SERIAL switched to HARD on the modem?

If you have checked those settings and they are all correct, try using the modem driver in Arduino firmware as an alternative way to register to network.

Follow [this](../research/hardware/ublox_modem/Arduino_ESP32/ESP32_Register/README.md) document. ***Note*** You will lose the MicroPython firmware and software, and you will need to repeat the [build process](micropython_build.md) again.

## Running Device Tests

The unit tests are stored [here](software/device/embedded/src/test/test_all.py). Run all the tests with:

```python
import unittest
unittest.main("test/test_all")
```

## Using the device interactively

As outlined in the [software architecture](./architecture/embedded_sw_architecture), we have two main modes - `regular mode` and `configure mode`. The REPL gives instructions on how to run these modes after you initate a soft boot.

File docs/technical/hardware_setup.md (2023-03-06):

# Hardware setup

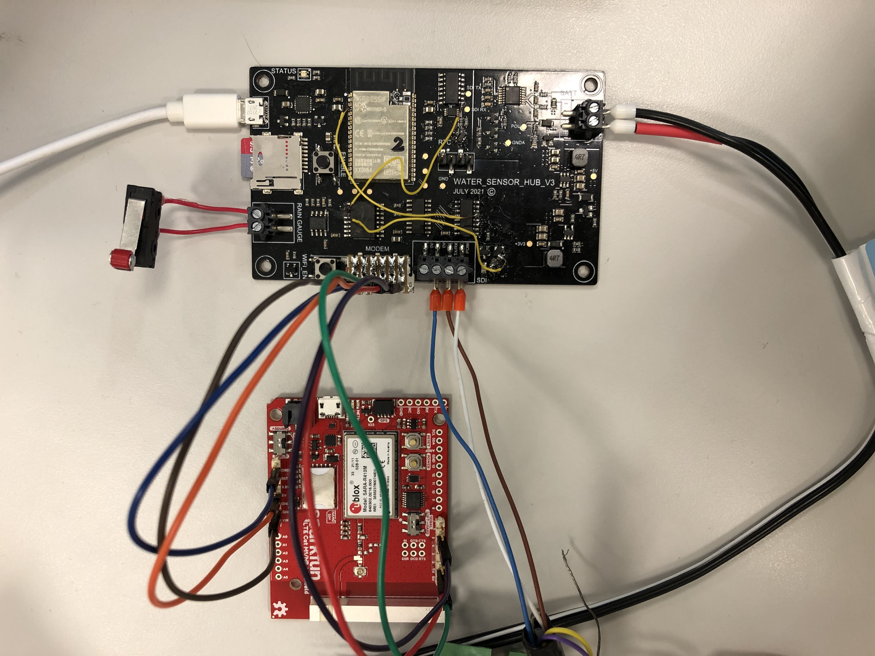
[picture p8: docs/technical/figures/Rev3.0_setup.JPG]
Hardware


## Power supply

The device can be powered by two source, 5V from USB and 12V from battery or power supply, and it can switch automatically. But keep in mind that some function requires 12V to work.

- 5V
  - Serial communication with ESP32
  - SD card
  - Rain gauge counter
  - RTC
- 12V
  - SparkFun LTE Cat M1/NB-IoT Shield
  - SDI-12

### SDI-12

SDI-12 sensor colour-coding

- White: Power
- Brown: TX/RX
- Blue: GND

### Rain gauge

The rain gauge acts as a switch, so connect both sides of the switch to the terminal.

### SparkFun SARA-R4 LTE CAT M1/NB-IoT Shield

Mobile communication is provided by a u-blox SARA-R4 Series module [1] via a SparkFun LTE CAT M1/NB-IoT Shield [2]. The SparkFun Shields are available for purchase with Hologram Global IoT SIM cards [3] which allow connection to the local cellular network under a prepay plan [4]. Technical information on the shield, including schematics, is available from GitHub [5] and the schematics and hookup guide are available from this repository in the [docs/datasheets/SparkFun LTE Cat M1 NB-IoT Shield/](docs/datasheets/SparkFun LTE Cat M1 NB-IoT Shield/) directory. The u-blox  SARA-R4 Series Data Sheet, System Integration Manual, AT Command Manual and other technical information specific to the module used in the current revision of the data recorder are available from the [docs/datasheets/u-blox SARA-R4 Modem/](docs/datasheets/u-blox SARA-R4 Modem/) directory.

1. u-blox SARA-R4 Series <https://www.u-blox.com/en/product/sara-r4-series>
1. SARA-R4 <https://www.sparkfun.com/categories/tags/sara-r4>
1. SparkFun LTE CAT M1/NB-IoT Shield - SARA-R4 (with Hologram SIM Card) <https://www.sparkfun.com/products/15087>
1. Hologram <https://www.hologram.io>
1. SparkFun LTE CAT M1/NB-IoT Shield - SARA-R4 <https://github.com/sparkfun/LTE_Cat_M1_Shield>

#### Required Manual Setup

Plug in the SIM card and:

- set the `PWR_SEL` switch to `ARDUINO`;
- set the `SERIAL` switch to `HARD`.

Use wires to connect the SparkFun SARA-R4 Shield with the Revision 3.1 PCB according to the following pin map

| Revision 3.1 Board | SparkFun Shield | Description       |
| ------------------ | --------------- | ----------------- |
| 0V                 | GND             | Ground            |
| 3.3V               | IOREF           | Reference voltage |
| 5V                 | 5V              | Power             |
| TX                 | RX              | Data exchange     |
| RX                 | TX              | Data exchange     |
| EN                 | 5               | Enable            |

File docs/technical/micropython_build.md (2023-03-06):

# MicroPython Build Docs

These instructions are intended to assist deploying custom MicroPython firmware to an ESP32, based on the MicroPython Wiki [1,2]. There are additional instructions available for building MicroPython for ESP32 in Docker [3,4] and several examples on the MicroPython Forum [5].

The advantage of building custom firmware is that it can be configured for a specific purpose, the benefit for the data recorder is that library modules can be added directly to the firmware rather than copied separately to the flash memory in a `lib` directory.

## References

1. Getting Started <https://github.com/micropython/micropython/wiki/Getting-Started>
1. Building Micropython Binaries <https://github.com/micropython/micropython/wiki/Building-Micropython-Binaries>
1. MicroPython Build Environment for ESP32 in a Docker Container <https://forum.micropython.org/viewtopic.php?t=7307>
1. micropython/build-micropython-esp32 <https://hub.docker.com/r/micropython/build-micropython-esp32>
1. Building micropython with 240mhz <https://forum.micropython.org/viewtopic.php?t=12586>

## Download MicroPython

```shell
git clone https://github.com/micropython/micropython.git
cd micropython
```

## Build mpy-cross

```shell
cd mpy-cross
make
```

## Set up ESP toolchain

```shell
cd ports/esp32
make ESPIDF= # make a note of the latest non-experimental hash
export ESPIDF=$HOME/esp/esp-idf # use any path provided it doesn't contain spaces
mkdir -p $ESPIDF
cd $ESPIDF
git clone https://github.com/espressif/esp-idf.git $ESPIDF
git checkout <Current supported ESP-IDF commit hash>
git submodule update --init --recursive
export IDF_PATH=$ESPIDF
```

You may want to add  ESPIDF to your .bashrc file so it is set up everytime you start your terminal.

```shell
echo "export ESPIDF=$HOME/esp/esp-idf" >> ~/.bashrc # optional
echo "export IDF_PATH=$ESPIDF" >> ~/.bashrc # optional
```

## Set up a Python virtual environment

```shell
cd ports/esp32 # in MicroPython repo
python3 -m venv build-venv
source build-venv/bin/activate
pip install --upgrade pip
pip install wheel # if it's not already installed
pip install -r $ESPIDF/requirements.txt
```

To start this environment later, you need to source the activate script again.

```shell
cd ports/esp32
source build-venv/bin/activate
```

## Continue setting up toolchain

Install dependencies:

```shell
sudo apt-get install gcc git wget make libncurses-dev flex bison gperf python python-pip python-setuptools python-serial python-cryptography python-future python-pyparsing libffi-dev libssl-dev libncurses5-dev libncursesw5-dev
```

Download the file available [here](https://docs.espressif.com/projects/esp-idf/en/v3.3.2/get-started/linux-setup.html#toolchain-setup). If you copy the link, you can download in the terminal.

```shell
cd $ESPIDF
wget <download_link> # skip this if you already downloaded it
tar -xzf <downloaded_file>
rm <downloaded_file>
```

Create an alias to activate the toolchain.

```shell
echo "alias get_esp32='export PATH=\"$HOME/esp/xtensa-esp32-elf/bin:$PATH\"'" >> ~/.profile
source ~/.profile
```

Now when you call `get_esp32`, the toolchain will be added to your PATH.

## Test serial connection

Connect the ESP32 devkit to your computer and find the port it is connected to.
You can do this by disconnecting and reconnecting the devkit and seeing which port changes.

```shell
ls /dev/tty*
```

Make a note of the port being used.

If using WSL or MacOS, install [this driver](https://www.silabs.com/products/development-tools/software/usb-to-uart-bridge-vcp-drivers). In Windows, open Device Manager, and identify the COM port.
The port will be named `COMx` so use `/dev/ttySx` for all commands in WSL.

You may need to add the user to `dialout`.

```shell
sudo usermod -a -G dialout $USER
```

Test the connection by starting a serial connection with a baudrate of 115200, 8 data bits, 1 stop bit, no parity, and XON/XOFF flow control.
I recommend using PuTTY (GUI) or picocom (CLI). You can install picocom on Linux with `sudo apt install picocom`.

The picocom command is `picocom --b 115200 /dev/ttyX` where `X` is replaced with the port number.

Reboot the board and you should see the ESP32 log printed out.
If there is no log, ensure you have pressed the correct button to reboot the board and that the port is correct.
If the log isn't legible, you may have set one of the serial parameters incorrectly.

Finish by closing the serial connection.

## Test an example build (not MicroPython)

```shell
cd $ESPIDF
cp -r $IDF_PATH/examples/get-started/hello_world .
cd $ESPIDF/hello_world
make menuconfig
```

If `make menuconfig` is successful, you should see a menu.
Change the Default serial port in Serial flasher config to the port the board is connected to.
Press Save and Exit.

With the device connected, build and flash the application.

```shell
make flash
```

This may take a while, but once it finishes you should be able to view the device printing "Hello world!" on the serial port and restarting.
To rebuild the application, you can just run `make app` or `make app-flash` to flash it too.

## Configuring MicroPython build

```shell
cd ports/esp32
touch makefile
```

Name the file `GNUmakefile` if you're on a case-sensitive filesystem.

In `makefile`, add the following lines:

```makefile
ESPIDF ?= $ESPIDF
BOARD ?= GENERIC_SPIRAM
#PORT ?= /dev/ttyUSB0
#FLASH_MODE ?= qio
#FLASH_SIZE ?= 4MB
#CROSS_COMPILE ?= xtensa-esp32-elf-

include Makefile
```

Make sure the submodules are up to date.

```shell
git submodule update --init
make clean
make
```

You should now be able to upload the firmware to the board.

```shell
make erase
make deploy
```

If that is unsuccessful and you have ensured the port is specified correctly in the makefile (this may be an issue in WSL), you can run the `esptool.py` script provided in the `ports/esp32` directory.

```shell
esptool.py --chip esp32 --port /dev/ttyX erase_flash
esptool.py --chip esp32 --port /dev/ttyX write_flash -z 0x1000 build-GENERIC_SPIRAM/firmware.bin
```

Make sure to replace `ttyX` with the correct port number.

You should now be able to access the REPL on the device over serial.

```shell
picocom -b 115200 /dev/ttyX
```

## Adding libraries to the firmware Image

Simply copy the .py files to the `modules/` subdirectory.
This will make the build step freeze the python files into frozen bytecode, and then bake it into the image.
Easy!

---

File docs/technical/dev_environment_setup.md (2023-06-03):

# Development Environment Setup

Table of Contents:

- [Development Environment Setup](#development-environment-setup)
  - [Overview](#overview)
    - [Dependencies](#dependencies)
    - [Preferred IDE - Visual Studio Code](#preferred-ide---visual-studio-code)
  - [Setup Instructions](#setup-instructions)

These instructions are intended to help get a development environment set up.

We have successfully developed this project on Ubuntu 20.04, MacOS 1.15, and on Windows 10 through WSL (Ubuntu 20.04).

The embedded software is written in Python 3, and the Webapp code is written in Javascript.

## Overview

### Dependencies

The following dependencies are **required**:

- **git**
- **python 3.9** or greater
- **nodeJS v14.21.3** or greater (with **npm v8.6.0** or greater)
  - **It would be ideal to use the latest nodeJS version** (following are confirmed to be working):
    - Node.js 20.2.0
    - Node.js 19.9.0
    - Node.js 18.16.0
    - Node.js 17.9.1
    - Node.js 16.20.0
    - Node.js 15.14.0
    - Node.js 14.21.3

The following dependencies are **preferred**:

- **pyenv** for managing python versions. There's an automated installer [here](https://github.com/pyenv/pyenv-installer).
- **virtualenv** for managing virtual environments. If using `pyenv`, use [pyenv-virtualenv](https://github.com/pyenv/pyenv-virtualenv) too.

### Preferred IDE - Visual Studio Code

Any code editor that supports python and javascript is sufficient for this project - be aware that micropython has some libraries pre-baked that aren't availble in Pypi (such as `machine`), so linting plugins will fail to resolve their imports.

If using Windows, install the [Remote WSL extension](https://code.visualstudio.com/docs/remote/wsl-tutorial).

## Setup Instructions

Firstly, ensure the dependencies above are installed. The following resources are useful:

- **macOS**: Install `pyenv` with homebrew - `brew install pyenv`
- Install node with [Node Version Manager](https://github.com/nvm-sh/nvm).
- install virtualenv locally with `pip3 install --user virtualenv`

Clone the repository locally with git:

```bash
git clone git@gitlab.ecs.vuw.ac.nz:course-work/engr301/2023/group<n>/data-recorder.git
```

If using `virtualenv`, activate the virtual environment:

```bash
virtualenv venv --python=python3.9
source venv/bin/activate
```

A virtual environment is a tool to create isolated python environments, so that the libraries we install for the project won't affect the python installation on your OS.
Note that we've standardized on using the name `venv` as the local folder containing the virtual environment.

Install the python dependencies:

```bash
pip install -r requirements.txt
```

We use [pre-commit](https://pre-commit.com/) to automatically run python linting, git commit message linting, and other checks. It is enforced by CI. Install the hooks with:

```bash
pre-commit install
pre-commit install --hook-type commit-msg
```

From [a note](https://jorisroovers.com/gitlint/#using-gitlint-through-pre-commit) specifying why the second line is important:

> It's important that you run `pre-commit install --hook-type commit-msg`, even if you've already used `pre-commit install` before. `pre-commit install` does **not** install commit-msg hooks by default!

Next, set up the Webapp development environment by following the instructions [here](/software/device/webapp/README.md).

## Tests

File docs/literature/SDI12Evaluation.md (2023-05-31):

# SDI12 Evaluation

All standards and protocols are taken from [SDI12 Documentation](https://www.sdi-12.org/current_specification/SDI-12_version-1_4-Jan-30-2021.pdf)

## Electrical Interface

The SDI-12 electrical interface requires 3 main lines:

- Serial Data Line: To read and write data to and from sensors and the data recorder.
- The Ground Line
- The 12V Voltage Line

The data recorder has these 3 lines implemented as a header on the PCB labeled as SDI_Pow for the 12V line, SDI12 for the data line and GND for the ground line.

### Serial Data Line

The serial data line is required to be bidirectional and three-state. During the investigation of the reading and writing capabilities of the SDI12 line, we were able to write to any sensor along the data line asking for their address and we could then read each address of each sensor. This confirmed the bidirectional functionality of the data line. The three-state functionality was already implemented with the 3-stage CMOS buffer in hardware/schematics/sdi-12.kicad_sch. The 3-stage CMOS buffer allows the data recorder, in the first stage, to receive data, in the second stage, amplify the signal and read it and finally in the third stage write back to the sensors. We can therefore conclude the current serial data line is SDI12 compliant.

#### Voltage Transitions

We did not test the data line voltage slew rate, to be compliant it must not be greater than 1.5V per microsecond.

#### Impedance

During our testing, we saw no reason why the sensors on the SDI12 bus would ever need to be turned off. By doing this, we assume that if the sensor wants to be turned off it is fully removed and, if the sensor is connected to the data line, it is on and transmitting. To meet SDI12 impedance protocols, the variable transistor between the data line and the 3-stage CMOS buffer must be between 500 and 1500 ohms when the transmitter is on. With the added transient protection during our testing, found in hardware/schematics/sdi-12-transient-protection_.kicad_sch, the additional resistor is 510 ohms between the 3-stage CMOS buffer and the serial data line. As we are assuming the sensors are always on and transmitting, this falls within the 500-1500 ohm range and, therefore, makes the data recorder SDI12 compliant for impedance.

### Ground Line

The ground line must be connected to both circuit ground and earth ground at the data recorder. As we were not deploying the device for any testing this was confirmed as outside of the scope of this project.

#### Transient Protection

The suggested transient protection circuit in Appendix A of the docs was added to hardware/schematics/sdi-12-transient-protection_.kicad_sch. The addition involved the breaking of the connection between the 3-stage CMOS buffer and the output header on the PCB, the transient protection is placed inbetween these connections. Additional circuitry was added to the schematics and any parts that were not in the symbol library were created and added to the library. The additional circuitry is compliant with SDI12 protocols and makes the data recorder compliant with SDI12 transient protection.

### 12-Volt Line

The 12V voltage line is required to provide between 9.6 and 16 volts, with respect to ground, at all times. The voltage supply does not have to be supplied by the data recorder itself and can be supplied by an external power supply. In our testing, we found that with multiple sensors connected along the 12V line, 12V was still being supplied to each sensor. Therefore, we can assume we can use the data recorder as our 12V supply and an external power supply is not necessary. While measuring the voltage in each configuration of the data recorder we noticed the 12V would dip just after initialization. An edit to the code was made to amend this and the 12V line now outputs 12V at all times regardless of the state of the data recorder. We did not test the maximum sensor load. We can conclude the 12V Voltage Line is compliant with the tested SDI12 protocols.

### Connectors

There is no specified connector for SDI12 compliance, the current header we are using on the PCB allows for easy switching of sensors connected to the heading and is easy to extend to allow multiple sensor connections.

## Communications Protocol/Software

Two changes were made to the software as part of the SDI-12 evaluation.

### Function to send arbitrary commands

A function was added to the driver `sdi12.py` which could send any command on the SDI-12 line. The existing function for sending commands includes checks to make sure the command was prefixed with a sensor address. This means it couldn't be used to send the command "?!" which queried all sensors on the line for their addresses. The function being added means this command can be sent.

### Stopping 12V line turning off during SDI-12 initialization

The `init_sdi()` function was found to always turn off the sensors when it was called by turning off the 12V line. To keep the sensors powered, a constant 12V must be provided at all times. Furthermore, the `pipeline()` function in `main.py` was found to turn the sensors back on several lines after calling `init_sdi()`. The `init_sdi()` function was modified so that it could be passed a 0 or 1 to turn the 12V line and thus the sensors on or off. Wherever the `init_sdi()` function was called was replaced with `init_sdi(0)` to keep the behaviour the same, except for `pipeline()` where it was changed to `init_sdi(1)` to turn the sensors on from the start.

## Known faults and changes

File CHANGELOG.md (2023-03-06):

# Change Log

## Revision 4.0 (May 2022)

### New Features

- SDI-12 operation is driven solely by the ESP32; the I/O extender is no longer used for SDI-12 functions.
- The rain gauge counter is directly connected to the I/O extender, allowing the bucket tip count to be read over the I2C bus.
- Adds header blocks for secure connection of the SparkFun SARA-R4 LTE CAT M1/NB-IoT Shield to the underside of the main board.
- Operational cellular network connection via the ublox SARA-R410M-02B cellular module and Hologram SIM on the SparkFun Shield.
- Data transmission by MQTT protocol to test server implemented.

### Bug Fixes

- Use the correct footprint for N-MOSFETs`Q501` and `Q502`on the PCB layout, restoring their original orientation.
- Remove the multiplexer from the rain gauge circuit, reducing the IC count by one.
- Reverse polarity protection for 12 V supply functions as intended.

## Revision 3.1 (October 2021)

<!--
Shown in the current photograph in the [Hardware Setup](docs/technical#hardware-setup) section of the technical docs.
-->

### Bug fixes

Operating as intended by making the following physical modifications to the PCB:

- Rotate N-MOSFETs `Q501` and `Q502` 120 degrees on the manufactured PCB to work-around the footprint mismatch.
- Use a jumper wire to connect a pull-down resistor to the multiplexer output, allowing the ESP32 bootloader to run on startup.
- Use jumper wires to connect spare output pins on the I/O extender to `SDI_EN` and  `SDI_FOut`; update SDI-12 driver to use I/O extender for `SDI_EN` and  `SDI_FOut`.

### Documentation

- H. Li, _Development of an IoT system for Environmental Monitoring_, Honours Report, Victoria University of Wellington (2021).

## Revision 3.0 (September 2021)

### New features

- Single-board PCB design based on surface-mount components.
- Tipping bucket rain gauge interface and counting circuit.
- Terminal block interface for UART connection to an external modem.
- Terminal block interface for I2C bus.

### Known Problems

Non-operational due to the following issues:

- N-MOSFET `Q501` and `Q502` are incorrectly connected due to an incorrect footprint in the PCB layout.
- ESP32 unable to enter bootloader on startup due to multiplexer direct connection to ESP32 `GPIO2`.
- ESP32 `GPIO34` and `GPIO35` are connected as outputs `SDI_EN` and  `SDI_FOut` to the SDI-12 interface circuit, but `GPIO34` and `GPIO35` are input-only pins.
- Reverse polarity protection amended but still does not protect the board from damage if the power is misconnected.

## Revision 2.0 (November 2020)

Final revision of the 2020 project using an ESP32 DevKit-C and header board configuration.

### New features

- SDI-12 interface via expansion board headers and driver
- External 12 V power on SDI-12 expansion board.
- Modem interface headers on main board holding the ESP32-DevKit-C.

### Known Problems

- Reverse polarity protection on 12 V power input does not protect the board from damage if the power is misconnected.

### Documentation

- J. Behrent, _Development of an IoT System for Environmental Monitoring_, Honours Report, Victoria University of Wellington (2020)
- B. Secker, _Development of an IoT System for Environmental Monitoring: Software_, Honours Report, Victoria University of Wellington (2020)

---

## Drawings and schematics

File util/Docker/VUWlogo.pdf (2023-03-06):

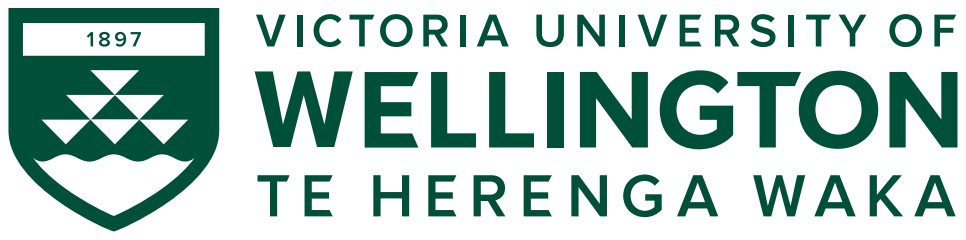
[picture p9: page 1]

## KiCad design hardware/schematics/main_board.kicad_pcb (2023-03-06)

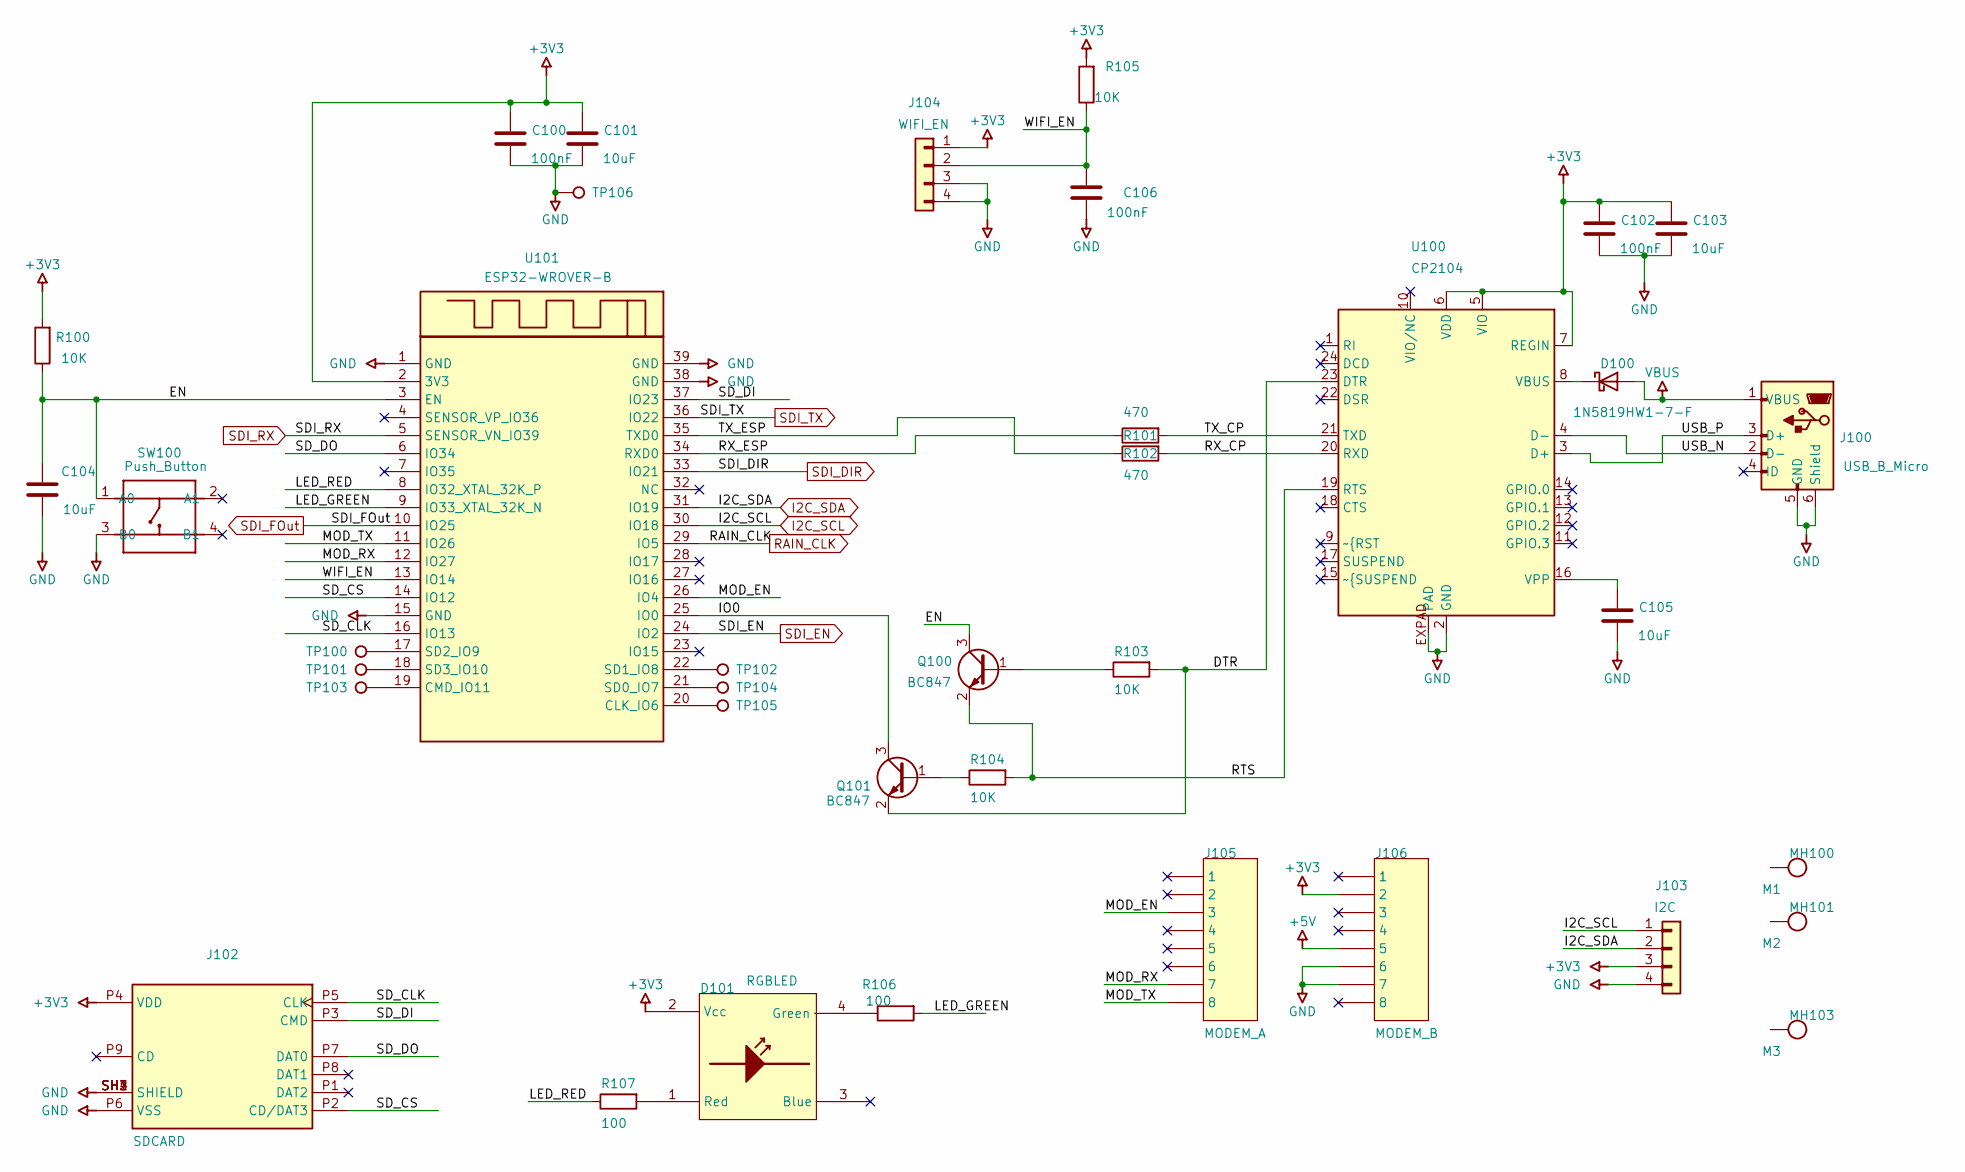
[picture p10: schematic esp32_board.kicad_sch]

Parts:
C100, C102, C106: 100nF; CAPC1608X80N
C101, C103, C104, C105: 10uF; CAPC2012X90N
D100: 1N5819HW1-7-F; SODFL3700X115N
D101: RGBLED; LED_APTF1616SEEZGQBDC_SM; MANUFACTURER PART NO APTF1616SEEZGQBDC
J100: USB_B_Micro; CON_1050170001
J102: SDCARD; CON_MEM2075-00-140-01-A; PARTREV A
J103: I2C; CON_NPTC041KFXC-RC_SM
J104: WIFI_EN; CON_NPTC041KFXC-RC_SM
J105: MODEM_A; CON_0878980826_SM
J106: MODEM_B; CON_0878980826_SM
MH100: M1; HOLN_M3
MH101: M2; HOLN_M3
MH103: M3; HOLN_M3
Q100, Q101: BC847; SOT95P240X130_123-3N
R100, R103, R104, R105: 10K; RESC1608X50N
R101, R102: 470; RESC1608X50N
R106, R107: 100; RESC1608X50N
SW100: Push_Button; SW_B3S-1000P_SM; MPN DTSM-62K-S-V-T/R(SN431)
TP100, TP101, TP102, TP103, TP104, TP105, TP106: RevPol; TP150
U100: CP2104; QFN50P400X400X90-25N
U101: ESP32-WROVER-B; IC_ESP32-WROVER

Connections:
+3V3: C100.1, C101.1, C102.1, C103.1, D101.2 (Vcc), J102.P4 (VDD), J103.3, J104.1, J106.2, R100.2, R105.1, U100.5 (VIO), U100.6 (VDD), U100.7 (REGIN), U101.2 (3V3); also elsewhere on the board
+5V: J106.5; also elsewhere on the board
/esp32_board/DTR: Q101.2 (E), R103.1, U100.23 (DTR)
/esp32_board/EN: C104.1, Q100.3 (C), R100.1, SW100.1 (A0), U101.3 (EN)
/esp32_board/IO0: Q101.3 (C), U101.25 (IO0)
/esp32_board/LED_GREEN: R106.1, U101.9 (IO33_XTAL_32K_N)
/esp32_board/LED_RED: R107.2, U101.8 (IO32_XTAL_32K_P)
/esp32_board/MOD_EN: J105.3, U101.26 (IO4)
/esp32_board/MOD_RX: J105.7, U101.12 (IO27)
/esp32_board/MOD_TX: J105.8, U101.11 (IO26)
/esp32_board/RTS: Q100.2 (E), R104.1, U100.19 (RTS)
/esp32_board/RX_CP: R102.1, U100.20 (RXD)
/esp32_board/RX_ESP: R101.2, U101.34 (RXD0)
/esp32_board/SD_CLK: J102.P5 (CLK), U101.16 (IO13)
/esp32_board/SD_CS: J102.P2 (CD/DAT3), U101.14 (IO12)
/esp32_board/SD_DI: J102.P3 (CMD), U101.37 (IO23)
/esp32_board/SD_DO: J102.P7 (DAT0), U101.6 (IO34)
/esp32_board/TX_CP: R101.1, U100.21 (TXD)
/esp32_board/TX_ESP: R102.2, U101.35 (TXD0)
/esp32_board/USB_N: J100.2 (D-), U100.4 (D-)
/esp32_board/USB_P: J100.3 (D+), U100.3 (D+)
/esp32_board/WIFI_EN: C106.1, J104.2, R105.2, U101.13 (IO14)
GND: C100.2, C101.2, C102.2, C103.2, C104.2, C105.2, C106.2, J100.5 (GND), J100.6 (Shield), J102.P6 (VSS), J102.SH1 (SHIELD), J102.SH2 (SHIELD), J102.SH3 (SHIELD), J102.SH4 (SHIELD), J103.4, J104.3, J104.4, J106.6, J106.7, SW100.3 (B0), TP106.1, U100.2 (GND), U100.EXPAD (PAD), U101.1 (GND), U101.15 (GND), U101.38 (GND), U101.39 (GND); also elsewhere on the board
I2C_SCL: J103.1, U101.30 (IO18); also elsewhere on the board
I2C_SDA: J103.2, U101.31 (IO19); also elsewhere on the board
unnamed: C105.1, U100.16 (VPP)
unnamed: D100.K, U100.8 (VBUS)
unnamed: D101.1 (Red), R107.1
unnamed: D101.4 (Green), R106.2
unnamed: Q100.1 (B), R103.2
unnamed: Q101.1 (B), R104.2
unnamed: TP100.1, U101.17 (SD2_IO9)
unnamed: TP101.1, U101.18 (SD3_IO10)
unnamed: TP102.1, U101.22 (SD1_IO8)
unnamed: TP103.1, U101.19 (CMD_IO11)
unnamed: TP104.1, U101.21 (SD0_IO7)
unnamed: TP105.1, U101.20 (CLK_IO6)
RAIN_CLK: U101.29 (IO5); also elsewhere on the board
SDI_DIR: U101.33 (IO21); also elsewhere on the board
SDI_EN: U101.24 (IO2); also elsewhere on the board
SDI_FOut: U101.10 (IO25); also elsewhere on the board
SDI_RX: U101.5 (SENSOR_VN_IO39); also elsewhere on the board
SDI_TX: U101.36 (IO22); also elsewhere on the board
VBUS: D100.A, J100.1 (VBUS); also elsewhere on the board

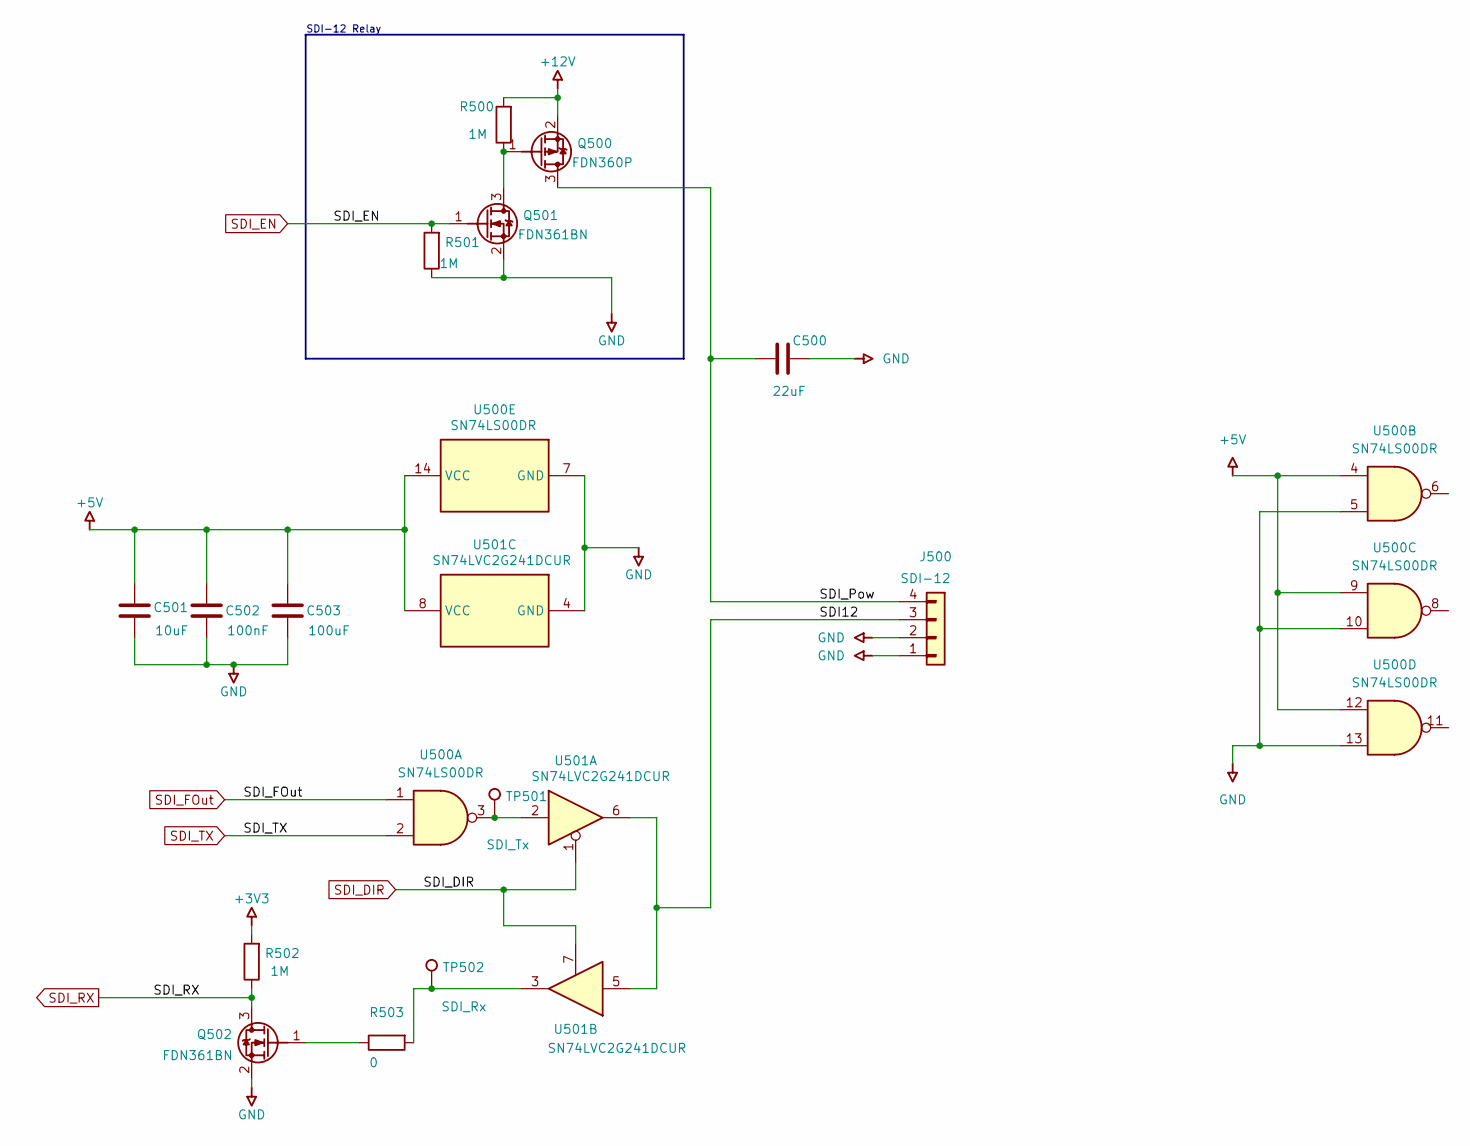
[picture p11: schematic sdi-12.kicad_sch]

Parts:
C500: 22uF; CAPC2012X90N
C501: 10uF; CAPC2012X90N
C502: 100nF; CAPC1608X80N
C503: 100uF; CAPC1608X80N
J500: SDI-12; CON_691508110304_SM
Q500: FDN360P; SOT95P240X110_123_SUPER-3N
Q501, Q502: FDN361BN; SOT95P240X110_231_SUPER-3N
R500, R501, R502: 1M; RESC1608X50N
R503: 0; RESC1608X50N
TP501: SDI_Tx; TP150
TP502: SDI_Rx; TP150
U500: SN74LS00DR; SOIC127P600X175-14N
U501: SN74LVC2G241DCUR; SOP50P320X90-8N

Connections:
+3V3: R502.1; also elsewhere on the board
+5V: C501.1, C502.1, C503.1, U500.4, U500.9, U500.12, U500.14 (VCC), U501.8 (VCC); also elsewhere on the board
+12V: Q500.2 (S), R500.1; also elsewhere on the board
/sdi-12/SDI12: J500.3, U501.5, U501.6
/sdi-12/SDI_Pow: C500.2, J500.4, Q500.3 (D)
GND: C500.1, C501.2, C502.2, C503.2, J500.1, J500.2, Q501.2 (S), Q502.2 (S), R501.2, U500.5, U500.7 (GND), U500.10, U500.13, U501.4 (GND); also elsewhere on the board
unnamed: Q500.1 (G), Q501.3 (D), R500.2
unnamed: Q502.1 (G), R503.2
unnamed: R503.1, TP502.1, U501.3
unnamed: TP501.1, U500.3, U501.2
SDI_DIR: U501.1, U501.7; also elsewhere on the board
SDI_EN: Q501.1 (G), R501.1; also elsewhere on the board
SDI_FOut: U500.1; also elsewhere on the board
SDI_RX: Q502.3 (D), R502.2; also elsewhere on the board
SDI_TX: U500.2; also elsewhere on the board

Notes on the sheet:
SDI-12 Relay

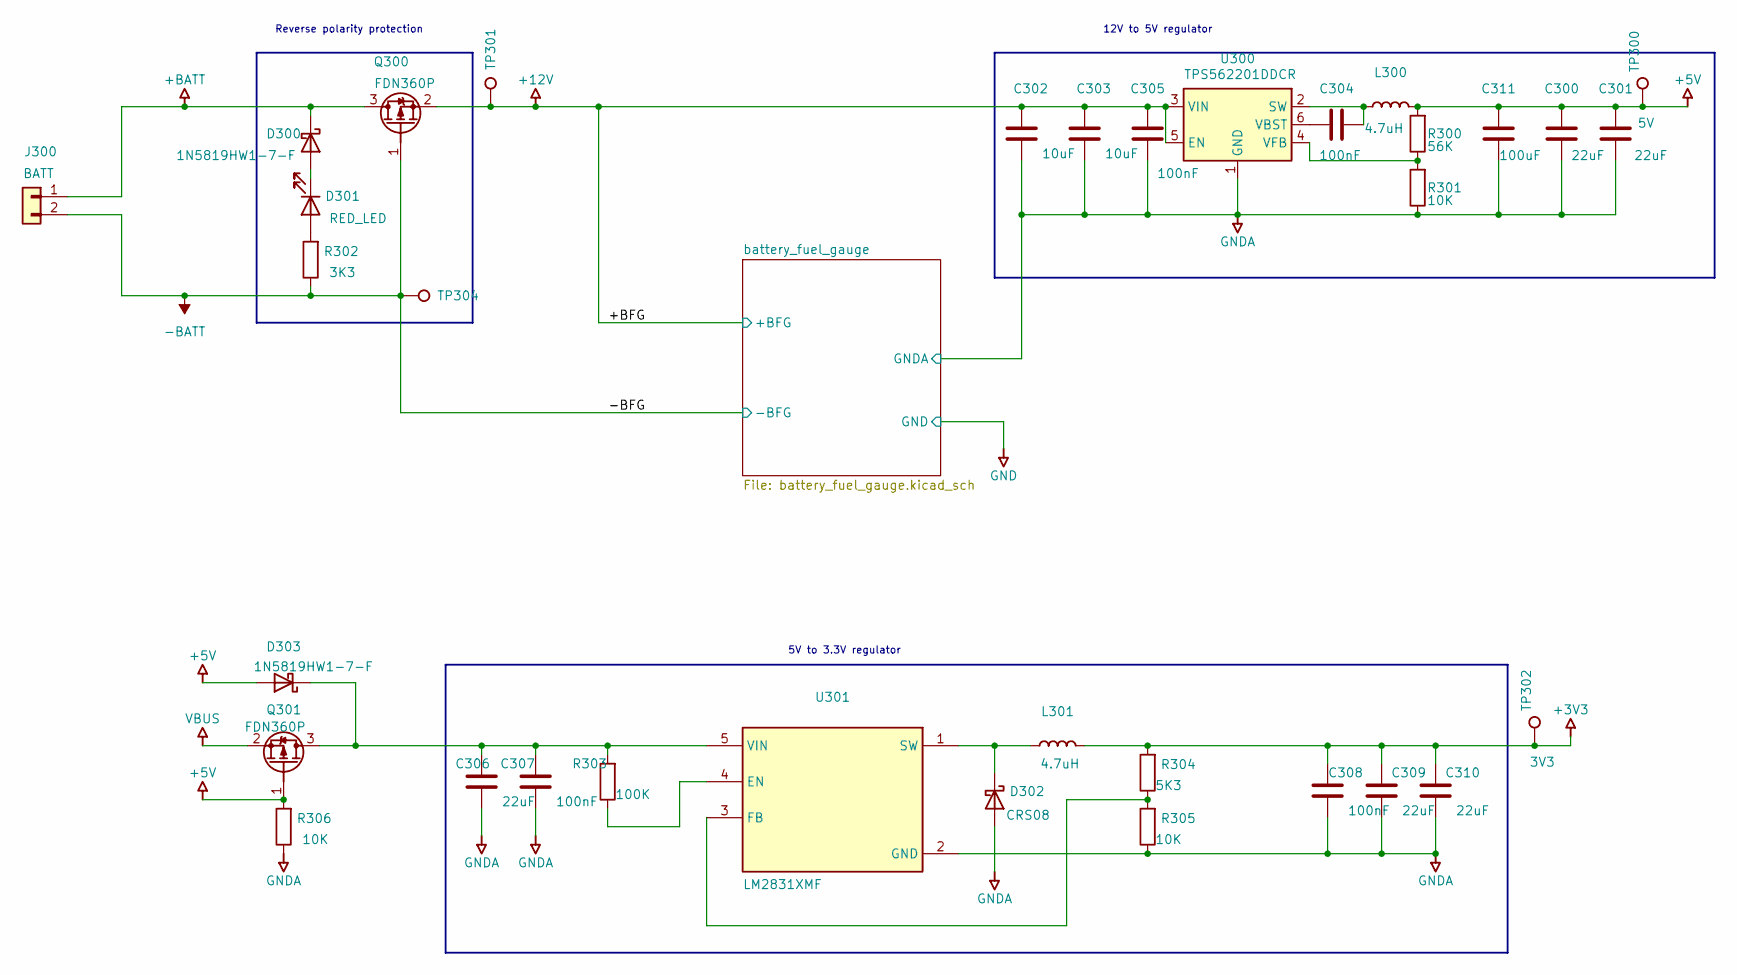
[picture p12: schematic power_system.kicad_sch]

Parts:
C300, C301, C306, C309, C310: 22uF; CAPC2012X90N
C302, C303: 10uF; CAPC2012X90N
C304, C305, C307, C308: 100nF; CAPC1608X80N
C311: 100uF; CAPC1608X80N
D300, D303: 1N5819HW1-7-F; SODFL3700X115N
D301: RED_LED; LED_19-217/B7C-ZL2N1B3X/3T_SM
D302: CRS08; SODFL3500X98N
J300: BATT; WURTH_691709710302
L300, L301: 4.7uH; IND_SRN5040-4R7M_SM
Q300, Q301: FDN360P; SOT95P240X110_123_SUPER-3N
R300: 56K; RESC1608X50N
R301, R305, R306: 10K; RESC1608X50N
R302: 3K3; RESC2012X50N
R303: 100K; RESC1608X50N
R304: 5K3; RESC1608X50N
TP300: 5V; TP150
TP301, TP304: RevPol; TP150
TP302: 3V3; TP150
U300: TPS562201DDCR; SOT95P305X110-6N
U301: LM2831XMF; SOT95P279X142-12345-5N

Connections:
+3V3: C308.1, C309.1, C310.1, L301.2, R304.1, TP302.1; also elsewhere on the board
+5V: C300.1, C301.1, C311.1, D303.A, L300.2, Q301.1 (G), R300.1, R306.2, TP300.1; also elsewhere on the board
+12V: C302.1, C303.1, C305.1, Q300.2 (S), TP301.1, U300.3 (VIN), U300.5 (EN); also elsewhere on the board
+BATT: D300.K, J300.1, Q300.3 (D)
-BATT: J300.2, Q300.1 (G), R302.2, TP304.1; also elsewhere on the board
GNDA: C300.2, C301.2, C302.2, C303.2, C305.2, C306.2, C307.2, C308.2, C309.2, C310.2, C311.2, D302.A, R301.2, R305.2, R306.1, U300.1 (GND), U301.2 (GND); also elsewhere on the board
unnamed: C304.1, L300.1, U300.2 (SW)
unnamed: C304.2, U300.6 (VBST)
unnamed: C306.1, C307.1, D303.K, Q301.3 (D), R303.1, U301.5 (VIN)
unnamed: D300.A, D301.K
unnamed: D301.A, R302.1
unnamed: D302.K, L301.1, U301.1 (SW)
unnamed: R300.2, R301.1, U300.4 (VFB)
unnamed: R303.2, U301.4 (EN)
unnamed: R304.2, R305.1, U301.3 (FB)
VBUS: Q301.2 (S); also elsewhere on the board

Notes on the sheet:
12V to 5V regulator
Reverse polarity protection
5V to 3.3V regulator

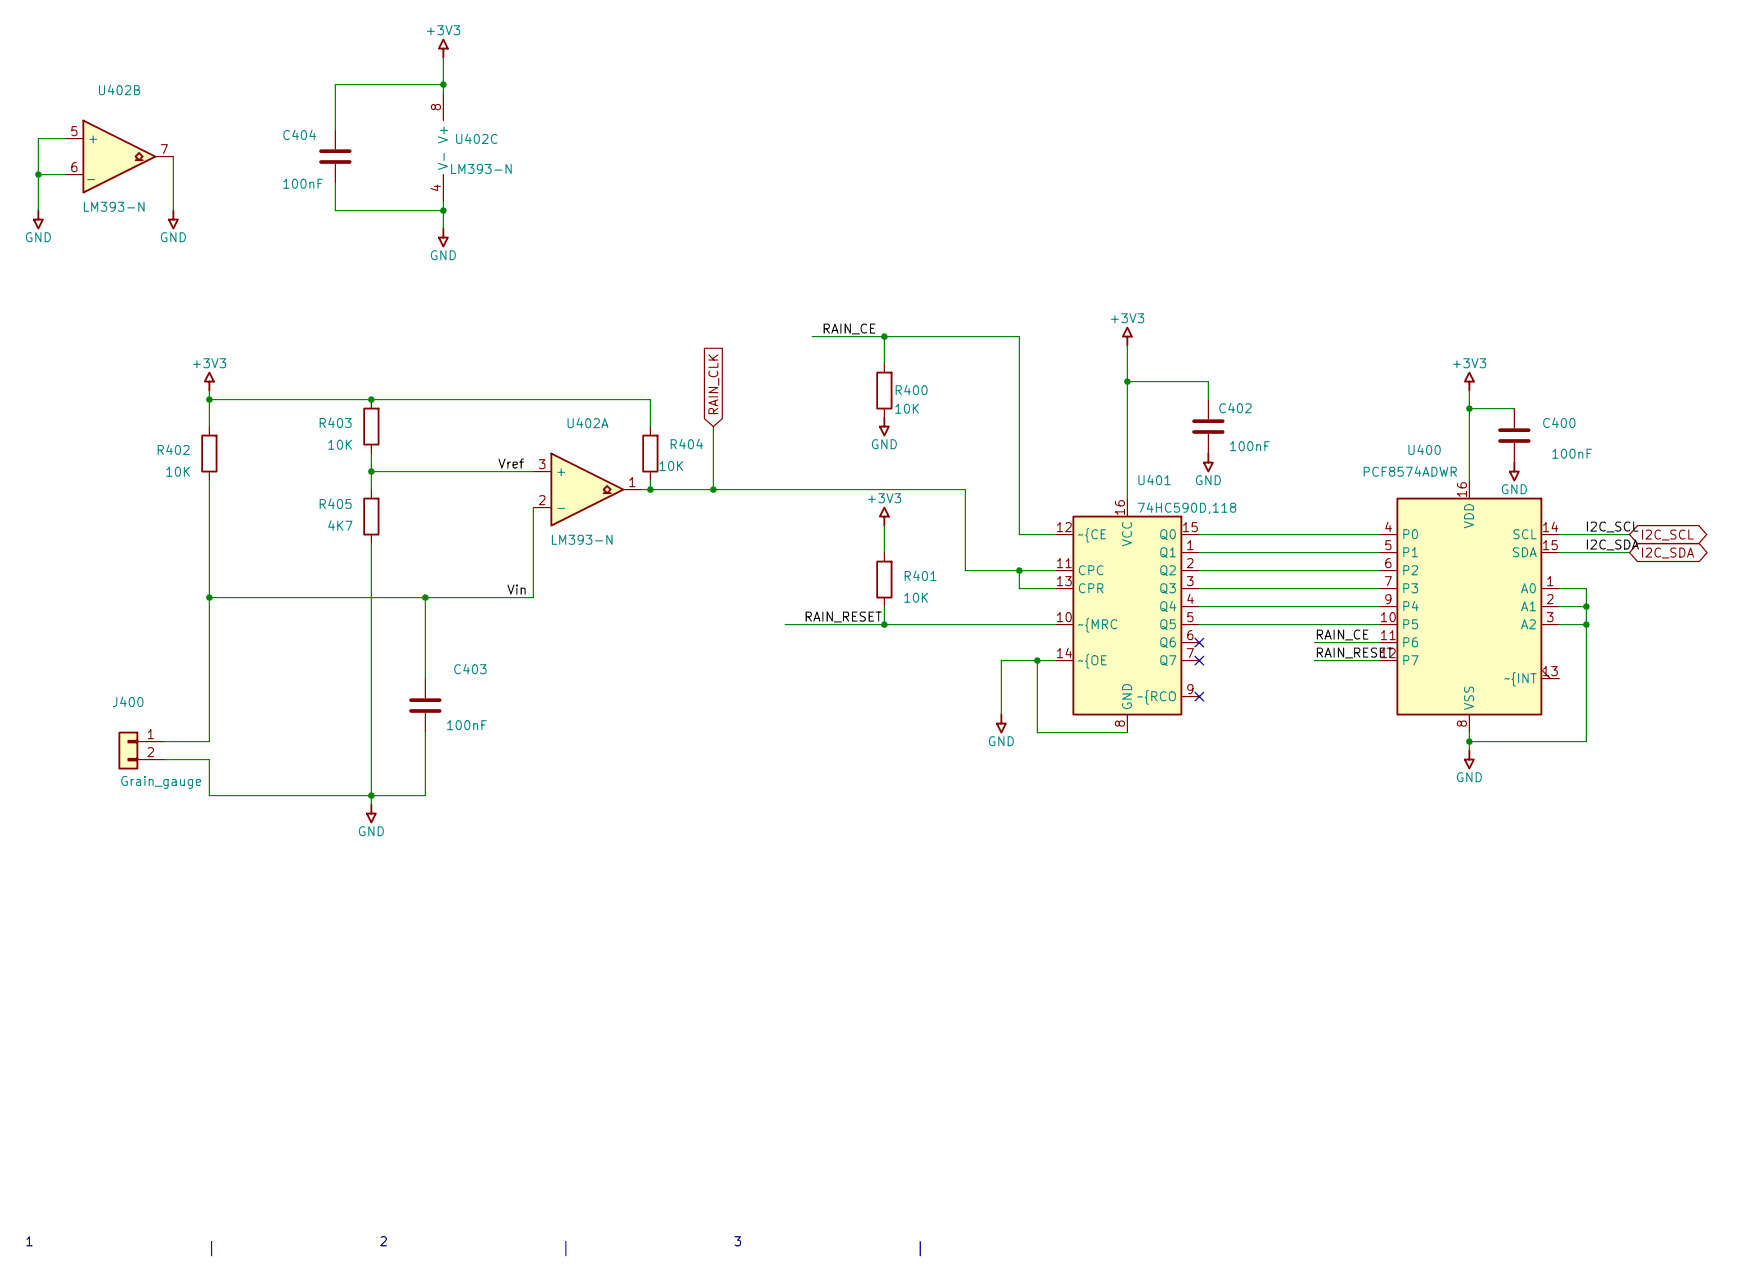
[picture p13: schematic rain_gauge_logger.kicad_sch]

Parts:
C400, C402, C403, C404: 100nF; CAPC1608X80N
J400: Grain_gauge; WURTH_691709710302
R400, R401, R402, R403, R404: 10K; RESC1608X50N
R405: 4K7; RESC1608X50N
U400: PCF8574ADWR; SOIC127P1030X265-16N
U401: 74HC590D,118; SOIC127P600X175-16N
U402: LM393-N; SOIC127P600X175-8N

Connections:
+3V3: C400.1, C402.2, C404.2, R401.1, R402.1, R403.1, R404.1, U400.16 (VDD), U401.16 (VCC), U402.8 (V+); also elsewhere on the board
/rain_gauge_logger/RAIN_CE: R400.1, U400.11 (P6), U401.12 (~{CE)
/rain_gauge_logger/RAIN_RESET: R401.2, U400.12 (P7), U401.10 (~{MRC)
/rain_gauge_logger/Vin: C403.2, J400.1, R402.2, U402.2 (-)
/rain_gauge_logger/Vref: R403.2, R405.1, U402.3 (+)
GND: C400.2, C402.1, C403.1, C404.1, J400.2, R400.2, R405.2, U400.1 (A0), U400.2 (A1), U400.3 (A2), U400.8 (VSS), U401.8 (GND), U401.14 (~{OE), U402.4 (V-), U402.5 (+), U402.6 (_), U402.7; also elsewhere on the board
I2C_SCL: U400.14 (SCL); also elsewhere on the board
I2C_SDA: U400.15 (SDA); also elsewhere on the board
unnamed: U400.4 (P0), U401.15 (Q0)
unnamed: U400.5 (P1), U401.1 (Q1)
unnamed: U400.6 (P2), U401.2 (Q2)
unnamed: U400.7 (P3), U401.3 (Q3)
unnamed: U400.9 (P4), U401.4 (Q4)
unnamed: U400.10 (P5), U401.5 (Q5)
RAIN_CLK: R404.2, U401.11 (CPC), U401.13 (CPR), U402.1; also elsewhere on the board

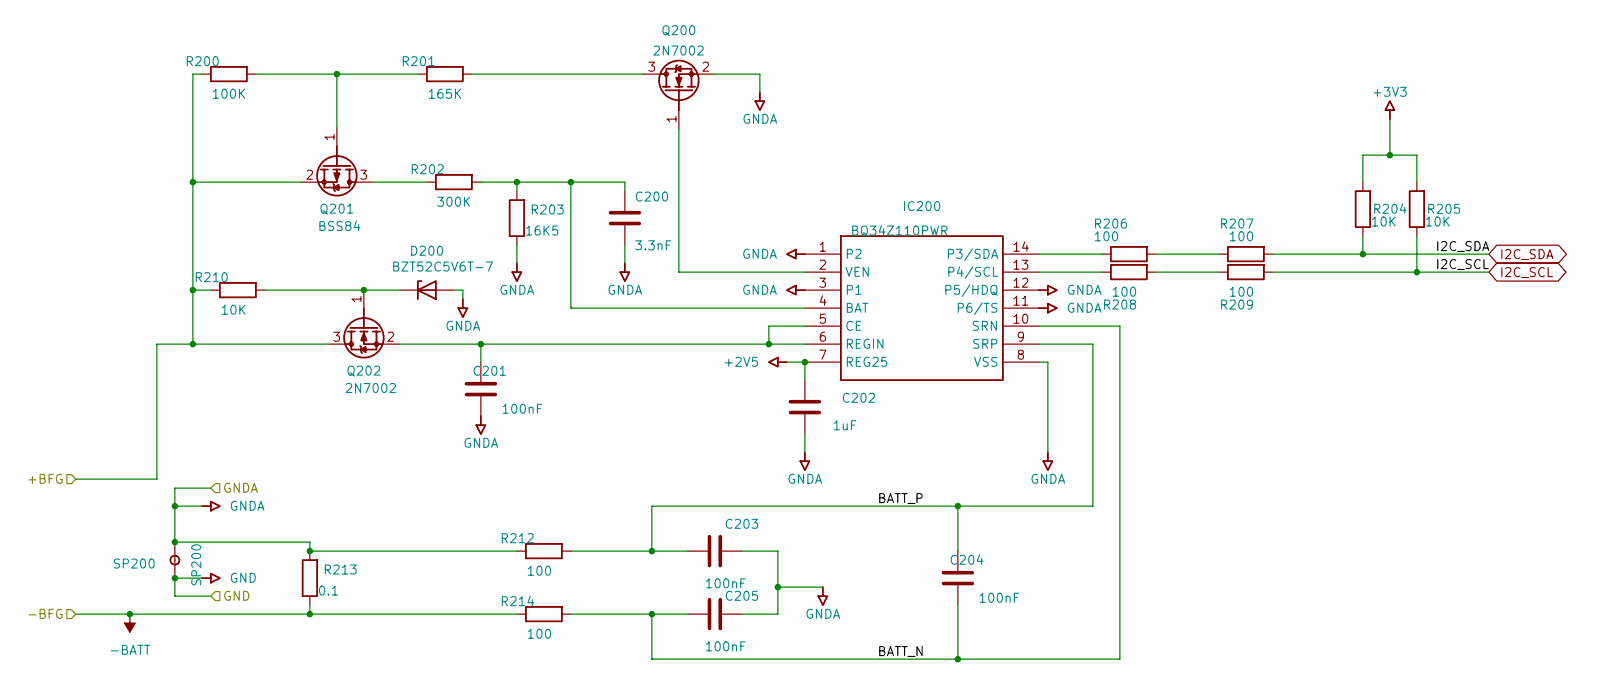
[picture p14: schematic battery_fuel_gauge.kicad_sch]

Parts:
C200: 3.3nF; CAPC1608X80N
C201, C203, C204, C205: 100nF; CAPC1608X80N
C202: 1uF; CAPC1608X80N
D200: BZT52C5V6T-7; SOD523
IC200: BQ34Z110PWR; SOP65P640X120-14N; MANUFACTURER_PART_NUMBER BQ34Z110PWR; MOUSER PART NUMBER 595-BQ34Z110PWR
Q200, Q202: 2N7002; SOT95P240X130_123-3N
Q201: BSS84; SOT95P240X130_123-3N
R200: 100K; RESC1608X50N
R201: 165K; RESC1608X50N
R202: 300K; RESC1608X50N
R203: 16K5; RESC1608X50N
R204, R205, R210: 10K; RESC1608X50N
R206, R207, R208, R209, R212, R214: 100; RESC1608X50N
R213: 0.1; RESC2012X50N
SP200: SP200; STAR_TH_2P

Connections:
+2V5: C202.2, IC200.7 (REG25)
+3V3: R204.1, R205.1; also elsewhere on the board
+12V: Q201.2 (S), Q202.3 (D), R200.1, R210.1; also elsewhere on the board
-BATT: R213.2, R214.1; also elsewhere on the board
/power_system/battery_fuel_gauge/BATT_N: C204.1, C205.2, IC200.10 (SRN), R214.2
/power_system/battery_fuel_gauge/BATT_P: C203.2, C204.2, IC200.9 (SRP), R212.2
GND: SP200.1; also elsewhere on the board
GNDA: C200.2, C201.1, C202.1, C203.1, C205.1, D200.A, IC200.1 (P2), IC200.3 (P1), IC200.8 (VSS), IC200.11 (P6/TS), IC200.12 (P5/HDQ), Q200.2 (S), R203.2, R212.1, R213.1, SP200.2; also elsewhere on the board
I2C_SCL: R205.2, R209.2; also elsewhere on the board
I2C_SDA: R204.2, R207.2; also elsewhere on the board
unnamed: C200.1, IC200.4 (BAT), R202.2, R203.1
unnamed: C201.2, IC200.5 (CE), IC200.6 (REGIN), Q202.2 (S)
unnamed: D200.K, Q202.1 (G), R210.2
unnamed: IC200.2 (VEN), Q200.1 (G)
unnamed: IC200.13 (P4/SCL), R208.1
unnamed: IC200.14 (P3/SDA), R206.1
unnamed: Q200.3 (D), R201.2
unnamed: Q201.1 (G), R200.2, R201.1
unnamed: Q201.3 (D), R202.1
unnamed: R206.2, R207.1
unnamed: R208.2, R209.1

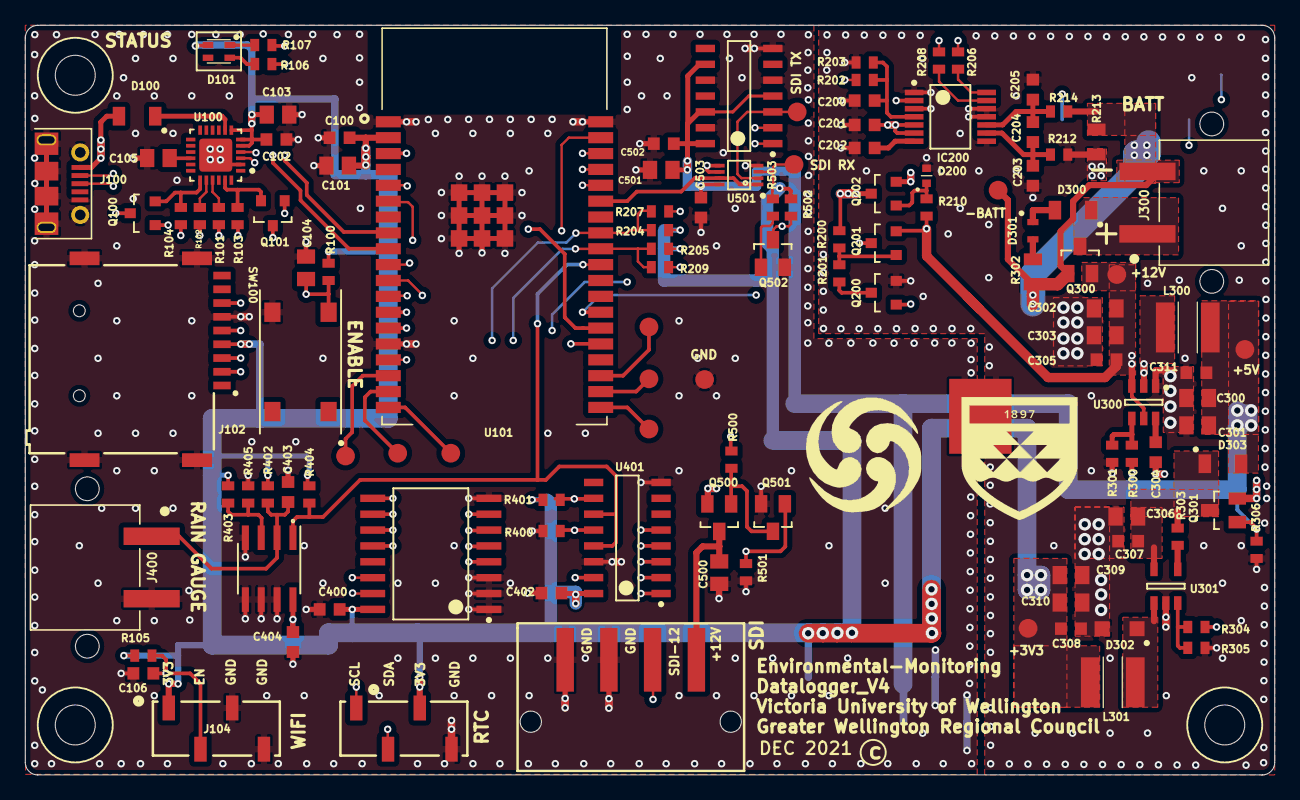
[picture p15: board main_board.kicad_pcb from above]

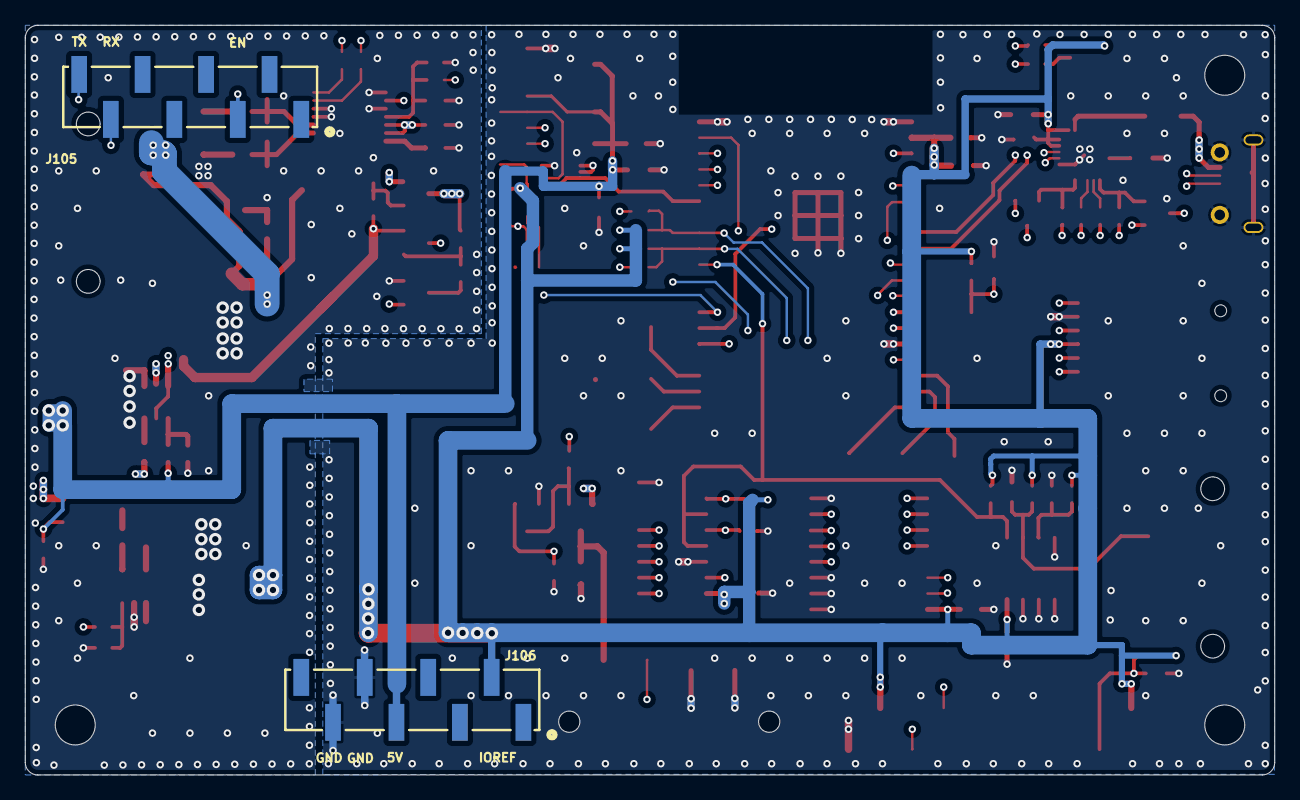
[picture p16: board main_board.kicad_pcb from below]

Board: 4 copper layers, 100.0 x 60.0 mm, 128 parts (2 on the bottom side), 87 nets.

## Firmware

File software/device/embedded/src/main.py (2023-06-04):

"""
Copyright (C) 2023  Benjamin Secker, Jolon Behrent, Louis Li, James Quilty

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

Executed on startup directly after boot.py
"""
import sys

# Change the module search order by modifying `sys.path`. The entry
# `""` specifies frozen bytecode. By moving this entry to the end
# of `sys.path`, frozen files will only be found if there is no
# match found in the filesystem.
# In the future this manipulation can be avoided by baking the
# `lib/` directory into the firmware.
if len(sys.path) > 0 and sys.path[0] == "":
    sys.path.append(sys.path.pop(0))

import logging

# threading module is used to enable concurent execution of the time synchronizing process, by creating a seperate thread for the sync task. Thus, code can keep running other tasks without sync to complete. Hence, the device will stay responsive
import threading

# importing rtc(Real time clock) from drivers for needed functions in time module
from drivers import rtc as rtc_driver

# Set global log level
# logging._level = logging.INFO
logging._level = logging.DEBUG

# Set Production status: affects display of development and console-only messages
# PRODUCTION = True
PRODUCTION = False

log = logging.getLogger("main")
# Enable the following to set a log level specific to this module:
# log.setLevel(logging.DEBUG)

log.info("Data Recorder booting...")

# TRACE-level debugging only:
# log.debug("Importing sdcard driver and mounting the card")
from drivers import sdcard as sdcard_driver

sdcard_driver.setup()

# uPy imports
# TRACE-level debugging only:
# log.debug("Importing uPy modules")
import machine
import esp32
from machine import Pin, deepsleep
from micropython import const, alloc_emergency_exception_buf

# lib imports
# TRACE-level debugging only:
# log.debug("Importing libraries")
try:
    import uasyncio as asyncio
except ImportError:
    import asyncio
import asyn
from aswitch import Pushbutton

import utime as time
import json

# code imports
# TRACE-level debugging only:
# log.debug("Importing drivers/services")
# from drivers import sdcard as sdcard_driver  # imported first-thing
from drivers import counter as counter_driver

from services import config as config_services
from services import sdi12 as sdi12_services
from services import scheduler as scheduler_services
from services import wlan as wlan_services

from util.time import isoformat
from util.buildinfo import log_build_info
from util import helpers

# TRACE-level debugging only:
# log.debug("Completed module and library imports")

# RGB LED pin connections
LED_RED_PIN = const(32)  # ESP32 GPIO 32 (physical pin 8)
LED_GREEN_PIN = const(33)  # ESP32 GPIO 33 (physical pin 9)
LED_BLUE_PIN = None  # Not connected in Rev::4.0; see #508.

# Time constants in seconds
DEEP_SLEEP_WAIT_PERIOD = 3
FIVE_MINUTES = 300
SIXTY_MINUTES = 3600

# Time constants in milliseconds
DEEP_SLEEP_PERIOD = 60000
SERVER_STOP_WAIT_PERIOD = 5000

# Recovery constants
RECOVERY_TRANSMISSION_COUNT = 3
MAX_RETRANSMIT_CACHE_SIZE = 1000 * 1000


# Allocate emergency ISR buffer - https://docs.micropython.org/en/latest/reference/isr_rules.html
alloc_emergency_exception_buf(100)

button_pin = Pin(14, Pin.IN, Pin.PULL_DOWN)
esp32.wake_on_ext0(pin=button_pin, level=esp32.WAKEUP_ALL_LOW)


async def start_server(server):
    """
    Coroutine to start the webserver
    Args:
        server: webserver object
    """
    server.run()


async def all_shutdown():
    await asyncio.sleep(1)


def deep_sleep(sensors: dict):
    """
    Go into deep sleep

    Args:
        sensors (dict): sensor objects to calculate sleep time for
    """
    sleep_time = scheduler_services.calculate_sleep_time(int(time.time()), sensors)
    log.info(
        "Entering deep sleep for {0} s ({1:.2g} minutes)".format(
            sleep_time, (sleep_time / 60)
        )
    )
    deepsleep((1000 * sleep_time) + 500)


async def stop_server(server, sensors):
    """
    Stop the server and go back into deep sleep after a short delay.

    This method is a callback for the sleep button

    Args:
        server: webserver object to be shut down gracefully
        sensors (dict): sensor objects to pass to deep_sleep()
    """
    set_client()
    # !!! It is uncertain why the following 5-second delay was inserted,
    # !!! initially in commit 25465623 to !111 via #193. It _may_ be necessary
    # !!! for the Tinyweb server to shut down cleanly. Defer removal until its
    # !!! function is understood.
    log.info(
        "Stopping the web server and entering deep sleep in {0} s".format(
            SERVER_STOP_WAIT_PERIOD / 1000
        )
    )
    await asyncio.sleep_ms(SERVER_STOP_WAIT_PERIOD)
    server.stop()
    deep_sleep(sensors)


def sync_time(modem):
    """Function to calibrate local time using modem or external RTC"""
    rtc = rtc_driver.rtc()

    def sync_rtc():  # new function that encapsulates existing time function and is designed to run on a seperate thread
        while True:
            try:
                current_timezone = (
                    time.timezone // 3600
                )  # Get the current timezone in hours
                if current_timezone == 12:
                    if modem.has_network:
                        network_time = modem.get_network_time()
                        time_start = time.ticks_ms()
                        network_mktime = time.mktime(network_time)
                        internal_RTC_offset = (
                            time.mktime(rtc.get_local_time()) - network_mktime
                        )
                        external_RTC_offset = (
                            time.mktime(rtc.get_ex_rtc_time()) - network_mktime
                        )
                        print("Internal RTC offset {:+d} s".format(internal_RTC_offset))
                        if abs(internal_RTC_offset) > 1:
                            rtc.set_local_time(network_time)
                            print("Synchronized internal RTC with network time")
                        print("External RTC offset {:+d} s".format(external_RTC_offset))
                        if abs(external_RTC_offset) > 1:
                            rtc.set_ex_rtc_time(network_time)
                            print("Synchronized external RTC with network time")
                    else:
                        print("Synchronizing time with external RTC module")
                        internal_RTC_offset = time.mktime(
                            rtc.get_local_time()
                        ) - time.mktime(rtc.get_ex_rtc_time())
                        print(
                            "Internal RTC offset from external RTC module {:+d} s".format(
                                internal_RTC_offset
                            )
                        )
                        if abs(internal_RTC_offset) > 0:
                            rtc.sync_rtc_time()
                else:
                    print("Device timezone is not set to UTC+12")
            except OSError:
                print("Failed to set time (OSError)")

            # Sleep for 1 hour before running the synchronization again
            time.sleep(3600)

    # Create a thread to run the synchronization process
    sync_thread = threading.Thread(target=sync_rtc)
    sync_thread.daemon = True  # Allow the program to exit even if the thread is running
    sync_thread.start()


def set_client():
    """Save new MQTT client profile"""
    log.info("Saving new MQTT client profile")
    from services import config
    from drivers import modem as modem_driver

    modem = modem_driver.Modem()
    modem.initialise()
    device_config = config.read_config_file()
    client_id = device_config["mqtt_settings"]["username"]
    server = device_config["mqtt_settings"]["host"]
    modem.mqtt_reset()
    modem.mqtt_set_client(client_id, server)
    modem.http_connect(modem_driver.MATTERMOST_SERVER)  # Modem connects to mattermost
    modem.power_off()


import asyncio


def regular_mode(device_config=None, device_data=None):
    """
    Enter Regular Mode.

    Regular mode is the usual, low-power mode of the device. It wakes up, gets an SDI-12 reading,
    Transmits the reading if it can and then goes back into deep sleep.

    Args:
        device_config (dict): device configuration dictionary
    """
    current_time = time.time()
    log.info("Entering Regular Mode")

    # Turn on red LED while in Regular Mode
    Pin(LED_RED_PIN, Pin.OUT, value=0)

    # Fetch device configuration if not provided
    device_config = device_config or config_services.read_config_file()
    # Fetch device data if not provided
    device_data = device_data or config_services.read_data_file()

    # Create a Counter object
    rain_counter = counter_driver.Counter()
    rainfall = rain_counter.get_rainfall()

    # Check schedule (if raining change interval to 5 minutes else 60 minutes)
    interval_minutes = 5 if rainfall > 0 else 60
    interval_seconds = interval_minutes * 60

    # Append rainfall and current time to device data
    device_data["rainfall"].append(rainfall)
    device_data["date_time"].append(current_time)

    # Determine if transmission should occur based on schedule
    should_transmit = scheduler_services.should_transmit(
        current_time,
        device_data["last_transmitted"],
        device_config["send_interval"] * interval_seconds,
    )

    if should_transmit:
        # Run the pipeline asynchronously to transmit data
        loop = asyncio.get_event_loop()
        try:
            loop.run_until_complete(pipeline(device_config, device_data, current_time))
        except (RuntimeError, TypeError, ValueError) as e:
            if not device_config["test_mode"]:
                # Log the error and handle exceptions
                log.critical("An error occurred in the pipeline: {0}".format(e))
                if not PRODUCTION:
                    try:
                        # Provide an opportunity to cancel deep sleep
                        print(
                            "\nDeep sleeping in {0} seconds.".format(
                                DEEP_SLEEP_WAIT_PERIOD
                            )
                        )
                        print(
                            "Press Ctrl-C to exit to the MicroPython interactive shell instead.\n"
                        )
                        time.sleep(DEEP_SLEEP_WAIT_PERIOD)
                    except KeyboardInterrupt:
                        # Prompt user with options upon interruption
                        print("Enter `regular_mode()` to take a sensor reading.")
                        print("Enter `configure_mode()` to start the webserver.")
                        print(
                            "Enter `deepsleep(ms)` to deep sleep for `ms` milliseconds.\n"
                        )
                        sys.exit()
                log.info(
                    "Entering deep sleep for {0} ms ({1:.2g} minutes)".format(
                        DEEP_SLEEP_PERIOD, (DEEP_SLEEP_PERIOD / 1000) / 60
                    )
                )
                deepsleep(DEEP_SLEEP_PERIOD)
    else:
        # Turn off red LED
        Pin(LED_RED_PIN, Pin.IN, None)
        if not PRODUCTION:
            try:
                # Provide an opportunity to cancel deep sleep
                print("\nDeep sleeping in {0} seconds.".format(DEEP_SLEEP_WAIT_PERIOD))
                print(
                    "Press Ctrl-C to exit to the MicroPython interactive shell instead.\n"
                )
                time.sleep(DEEP_SLEEP_WAIT_PERIOD)
            except KeyboardInterrupt:
                # Prompt user with options upon interruption
                print("Enter `regular_mode()` to take a sensor reading.")
                print("Enter `configure_mode()` to start the webserver.")
                print("Enter `deepsleep(ms)` to deep sleep for `ms` milliseconds.\n")
                sys.exit()
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

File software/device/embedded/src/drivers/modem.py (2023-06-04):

"""
Copyright (C) 2023  Benjamin Secker, Jolon Behrent, Louis Li, James Quilty

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

This module is use to handle basic modem operation by AT command

"""
import time
import json
import ure
from machine import UART, Pin
from util.time import isoformat

import logging

try:
    import uasyncio as asyncio
except ImportError:
    import asyncio
import asyn

log = logging.getLogger("modem")
# Enable the following to set a log level specific to this module:
# log.setLevel(logging.DEBUG)


MODEM_STANDARD_RESPONSE_TIMEOUT = 1000  # Standard AT command time out (ms)
MODEM_SET_BAUD_TIMEOUT = 10000  # Setting baud rate time out (ms)
MODEM_POWER_ON_PULSE_PERIOD = 300  # Low time to trigger power-on (ms)
MODEM_POWER_OFF_PULSE_PERIOD = 1750  # Low time to trigger graceful power-off (ms)
MODEM_MQTT_CONNECT_TIMEOUT = 120000  # MQTT connection time out (ms)

# Time constants in seconds
MODEM_MQTT_PING_PERIOD = 60  # Keep-alive period

# Suported AT Commands
# General
MODEM_COMMAND_AT = "AT"  # AT "Test"
MODEM_COMMAND_ECHO = "E"  # Local Echo
MODEM_COMMAND_IMEI = "+CGSN"  # IMEI identification
MODEM_COMMAND_IMSI = "+CIMI"  # IMSI identification
MODEM_COMMAND_CCID = "+CCID"  # SIM CCID
MODEM_COMMAND_OFF = "+CPWROFF"  # Turn off the modem
# Control and status
MODEM_COMMAND_FUNC = "+CFUN"  # Functionality (reset, etc.)
MODEM_COMMAND_CLOCK = "+CCLK"  # Clock
MODEM_COMMAND_AUTO_TZ = "+CTZU"  # Automatic time zone update
# Network service
MODEM_COMMAND_MNO = "+UMNOPROF"  # MNO (mobile network operator) Profile
MODEM_SIGNAL_QUALITY = "+CSQ"  # Signal quality
MODEM_REGISTRATION_STATUS = "+CREG"
MODEM_MESSAGE_PDP_DEF = "+CGDCONT"  # Network connection parameters (context definition)
MODEM_OPERATOR_SELECTION = "+COPS"  # Network operator info
MODEM_COMMAND_BAUD = "+IPR"  # Baud rate
# HTTP
MODEM_COMMAND_HTTP_CONTROL = "+UHTTP"  # HTTP Control
MODEM_COMMAND_HTTP_COMMAND = "+UHTTPC"  # HTTP Command
MODEM_COMMAND_HTTP_ERROR = "+UHTTPER"  # HTTP Error
# File
MODEM_COMMAND_FILE_WRITE = "+UDWNFILE"  # Write file to filesystem. Called "Download File" in ublox documentation, which can be confusing
MODEM_COMMAND_FILE_DELETE = "+UDELFILE"  # Delete file
MODEM_COMMAND_FILE_LIST = "+ULSTFILE"  # List all files in filesystem
MODEM_COMMAND_FILE_READ = "+URDFILE"  # Read file

# Response
MODEM_RESPONSE_OK = "OK"
MODEM_RESPONSE_ERROR = "ERROR"

# GPIO config
MODEM_POWER_PIN = 4
MODEM_TX_PIN = 27
MODEM_RX_PIN = 26

# Baud rate config
NUM_SUPPORTED_BAUD = 6
MODEM_SUPPORTED_BAUD = [115200, 9600, 19200, 38400, 57600, 230400]
MODEM_DEFAULT_BAUD = 115200

# HTTP temporary file on modem for POSTing MonitorMyWatershed data
HTTP_POST_DATA_FILE = "post_data.tmp"

# 2023 Data Recorder Webhook
MATTERMOST_WEBHOOK = "/hooks/3g7p6bm3ojfijpigdoers15awr"

MATTERMOST_SERVER = "https://mattermost.ecs.vuw.ac.nz"

MATTERMOST_CHANNEL_PATH = "/engr301-2023/channels/group-3-data-recorder"


class ModemTimeout(Exception):
    """Raised when modem commands time out"""


class ModemFileError(Exception):
    """Raised when the modem raises a file error"""
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

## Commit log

2023-04-11 fix(webapp): remove azure references
    [requirements.csv]
2023-05-03 feat(sdcard): Implement debug failed transmission writing on network failure
    Currently does not save to an actual file, but logs the save event in the log output. Allows for the sd card to be absent, but warns that failed transmissions will be lost
2023-05-04 chore(rain-gauge): changes obtained through fetch
    [requirements.csv]
2023-05-04 perf(sdcard): Change read_failed_transmission() to utilise os.scandir()
    os.scandir() generates a generator object, allowing for iteration of the directory without loading the entire file list into memory. This is important due to the limitations of the ESP32. This improv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
2023-05-04 feat(sdcard): Implement safety check to ensure SD card is mounted before loading cached recording files
2023-05-09 refactor(device-sw): use new conf in provision.py
2023-05-16 feat(webapp): filteration functionality implemented in history page
2023-05-16 feat(webapp): Added filter functionality in History Page
2023-05-17 docs(sdi-12): added script we used in repl loop to query addresses of sensors on sdi-12 line
2023-05-17 docs(sdi-12): included results of testing two sensors using address query script
2023-05-17 feat(rtc): Editted existing rtc method with new method that encapsulates and runs in different thread
2023-05-17 style(rtc): Editted existing rtc method with new method that encapsulates and runs in different thread, Formatted with Black
2023-05-18 fix(webapp): no longer tries to update device data
2023-05-21 feat(webapp): Added the toggle button onto the main page. Began adding in the colour variables into the individual style sheets - however will need to refine the current colour choices. Please note -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
2023-05-23 feat(webapp): Filter issue fixed
2023-05-23 docs(battery): created a file and filled with outline headers for battery fuel gauge retrospective
2023-05-23 feat(sdi-12): Added transint protection into the sdi-12 schematic, saved as a aseperate schematic.
    [sdi-12-transient-protection_.kicad_sch]
2023-05-24 docs(battery): background info in /docs/literature/BatteryFuelGaugeRetrospective.md started
2023-05-24 docs(battery): added writeup as to why we couldn't implement the battery fuel gauge
2023-05-24 feat(webapp): Finished the overall implementation of dark and light mode for the webapp. Finialised colour pallete. Branch just needs implementation for the Maintenance Mode Node Pop up and the Add S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
2023-05-24 docs(battery): Added to the BatteryFuelGaugeRetrospective
2023-05-25 docs(battery): editing the BatteryFuelGaugeRetrospective.md
2023-05-27 feat(webapp): Light and Dark mode UX fully implemented. In this commit, I implemented the styling for the Enable Maintenance Mode Pop up and the Add SDI-12 Sensor Pop Up. This issue and branch is now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
2023-05-27 docs(battery): added writeup on I2C communication, including code
2023-05-29 fix(webapp): lint-staged updated to 10.5.4
2023-05-30 fix(sdi-12): changed init_sdi() function to not always turn off sensors
2023-05-31 fix(sdi-12): added delay to more reliably read sensor response
2023-06-01 refactor(device-sw): refactored regular mode to remove redundant code and comments to improve readability
2023-06-02 fix(services): corrected modem unit test names, and added return to modem power_off
2023-06-03 chore(webapp): remove unnecessary code from the deviceconfig component
2023-06-03 chore(webapp): remove unnecessary code from the sensorconfig component
2023-06-03 refactor(device-sw): configure mode to remove redundant code and comments to improve readability
2023-06-03 build(webapp): update lint-staged to latest 10.5.4 -> 13.2.2
2023-06-04 fix(webapp): Add missing code in sensorconfig

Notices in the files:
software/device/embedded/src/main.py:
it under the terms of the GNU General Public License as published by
